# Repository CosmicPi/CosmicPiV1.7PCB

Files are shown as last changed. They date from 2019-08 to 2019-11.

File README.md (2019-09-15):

# CosmicPiV1.6
Version 1.6 of the Cosmic Pi, learning the lessons from V2 and going back to something simpler. All the components are now on a single PCB with a snap-off for the SiPM elements. We have also moved to KiCad!

The SiPM's in this design are from Ketek, and we're very happy with the performance. You can find the SiPM datasheet here: https://www.ketek.net/wp-content/uploads/2018/12/KETEK-PM3325-WB-D0-Datasheet.pdf
The SiPM's are also available to purchase retail from their shop (!) - a significant advance over our previous models:
https://www.ketek.net/store/products/pm3325-wb/

The design uses scintillators from Amcrys http://www.amcrys.com/ which are not yet available via a retail outlet, however any BC-408 equivalent scintillator that has diamond polished finish surfaces and dimensions of 200x100x10mm can be mated to the SiPMs with suitable mounting holes.

# What do the signals do?

Shapeout 1 & 2 - Shaped (i.e. amplified and stretched signal from the SiPMs - muon detection waveforms). Not used in current software.

Biasfb 1 & 2 - Feedback on the Vbias supply (i.e. to check that it's the right voltage). Not used in current software.

Inj led 1 & 2 - Light injector LEDs, allowing the operation of the SiPM to be checked (and calibrated) post-assembly. 

Accint 1, 2 - Interrupts from the accelerometer, not really used for anything yet.

Magint 3 - Interrupt from magnetometer, also not used.

Flag, boot0 - Signals to the Raspberry Pi, flag can be set by the STM32 to indicate a particular condition. Boot0 is used to set the boot mode of the STM32, for example when flashing. This doesn't function correctly in this version, it will be updated for V1.7, due to some issues with the STM32 bootloader.

Vbusm otg dm otg dp - Vbus is the USB bus voltage detection line to the STM32 (i.e. in OTG mode, sense incoming voltage), DM and DP are the differential lines for USB communication. Not functional in the current software; note that the USB doesn't power the device.

Swclk, swdio - These are the programming commands for the STM32, based on the ST-Link system. These work fine, used for programming.

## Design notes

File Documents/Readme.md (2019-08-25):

Here are some documents for the verification of the mechanical drawings. Your help is requested in checking the mechanical fit of our board with the holes we're getting machined in the box. Please take a look and share with us your comments about the mechanical design.

The board will be fixed to the chassis with 4 metal M3 thread screws with plastic washers. The front plate will be held in place by the structrure of the chassis.

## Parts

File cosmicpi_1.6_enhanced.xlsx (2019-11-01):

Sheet: Sheet1
Id | Designator | Supplier | SKY | Manufacturer | MPN (Manufacturer Part Number) | Quantity | Alternative | Comments | Package | Value | Voltage | Tolerance | Wattage
1 | D5,D6 | RS | 687-2779 | Taiwan Semi | BAS70-04 RF | 2 | BAS70-04LT1G |  | SOT-23 | BAS70-04
2 | R46,R47 | RS | 179-9597 | Panasonic | ERA3AEB512V | 2 | NTR06B5101CTR1KF |  | R_0603_1608Metric | 5100 |  | 1% | 100mW
3 | FL2, FL1 | RS | 770-7133 | Wurth | 744235220 | 2 | 123-4666 | Alternative is RS-PRO | IND_744232090 | EMI_Filter_CommonMode
4 | J14,J8,J11,J12 | RS | 701-9773 | Preci-Dip | 800-80-002-20-001101 | 4 | 830-80-002-20-001101 |  | PinHeader_1x02_P2.54mm_Horizontal | Conn_01x02_Male
5 | J9,J10,J13,J15 | RS | 766-6604 | Samtec | CES-102-01-T-S | 4 |  |  | PinHeader_1x02_P2.54mm_Vertical | Conn_01x02_Female
6 | D4,D3 | RS | 792-0787 | Nexperia | BAT46WH | 2 |  |  | D_SOD-123F | BAT46
7 | J2 | RS | 759-5299 | Molex | 73251-1150 | 1 |  |  | SMA_Molex_73251-1153_EdgeMount_Horizontal | SMA
8 | C27,C29,C34,C35,C64,C74,C14,C55,C54,C53,C50,C49,C44,C43,C66,C2,C5,C6,C7,C8,C72,C11,C12,C65,C23,C18,C70,C17,C15,C67 | RS | 669-8767 | Yageo | CC0603KRX7R9BB104 | 30 |  |  | C_0603_1608Metric | 100n | 50V
9 | C57 | RS | 915-9114 | TDK | C1608X5R1A226M080AC | 1 | GRM188R61A226ME15D |  | C_0603_1608Metric | 22u | 10V | 20%
10 | C30,C31,C41,C59,C22,C16 | RS | 616-9537 | Yageo | CC0603KRX7R9BB103 | 6 |  |  | C_0603_1608Metric | 10n | 50V
11 | C32,C33,C61,C60,C19 | Farnell | 722250 | Yageo | CC0603KRX7R8BB224 | 5 |  |  | C_0603_1608Metric | 220n | 25V
12 | C56,C13,C24 | RS | 884-7166 | Murata | GRM188B31A106ME69D | 3 |  |  | C_0603_1608Metric | 10u | 10V
13 | C46,C45 | RS | 815-1531 | Murata | GRM1885C2A300JA01D | 2 |  |  | C_0603_1608Metric | 30p | 100V
14 | C3,C4 | RS | 773-8446 | Syfer | 0603Y1000220JCT | 2 | CL10C220FB8NNND |  | C_0603_1608Metric | 22p | 16V | 5%
15 | C71,C73 | Farnell | 1828913 | Murata | GRM1885C1H102FA01D | 2 | GRM1881X1H102JA01D |  | C_0603_1608Metric | 1n | 50V | 5%
16 | C68,C69 | Farnell | 1414642 | Kemet | C0603C472K5RACTU | 2 | C0603C473K5RACAUTO |  | C_0603_1608Metric | 47n | 50V | 10%
17 | C47,C48 | Farnell | 2773209 | Kemet | C0805C104M3RACTU | 2 |  |  | C_0805_2012Metric | 100n
18 | C9,C10,C52,C51 |  |  |  |  | 4 |  | DNP | C_1206_3216Metric | n.a.
19 | C20,C75,C25,C62,C63,C58,C21,C28,C26,C40,C37,C38,C36,C39,C42 | Farnell | 9227873 | Kemet | C1206C105Z3VACTU | 15 |  |  | C_1206_3216Metric | 1u | 25V | -20%->+80%
20 | C76 | RS | 172-1612 | Taiyo Yuden | JMK316BBJ107MLHT | 1 |  |  | C_1206_3216Metric | 100u | 6.3V | 20%
21 | C1 | RS | 766-1037 | Samsung | CL21B475KOFNNNG | 1 | C0805C475K3PACTU |  | C_0805_2012Metric | 4.7u | 16V | 10%
22 | J1 | RS | 122-4879 | Wurth | 694106301002 | 1 |  |  | BarrelJack_Horizontal | Barrel_Jack_Switch
23 | J6 | Farnell | 2847171 | Multicomp | 2211SM-06G-B1-TB | 1 | TSM-106-01-T-SV |  | PinSocket_1x06_P2.54mm_Vertical_SMD_Pin1Left | SWD
24 | J7 | Farnell | 2847928 | Multicomp | 2214SM-20G-75-PCR | 1 | CLH-110-F-D-BE |  | PinSocket_2x20_P2.54mm_Vertical_SMD | Raspberry_Pi_2_3
25 | J3 | Farnell | 2293836 | Molex | 105017-0001 | 1 |  |  | USB_Micro-B_Molex-105017-0001 | USB_B_Micro
26 | J4, J5 |  |  |  | PM3325-WB | 2 |  | Customer Supplied | Ketek_PM3325-WB | SiPM1
27 | U3 | RS | 908-4108 | Quectel | L76-M33 | 1 | L70B-M39 |  | LM76-M33 | L76-M33
28 | Y1 | RS | 178-2555 | CTS | ATS08ASM-1E | 1 |  |  | Crystal:Crystal_SMD_HC49-SD | 8 MHz
29 | L3 | RS | 496-0978 | EPCOS | B82496C3470J000 | 1 |  |  | L_0603_1608Metric | 47nH
30 | L1 | RS | 604-1489 | TDK | MLZ1608A2R2MT | 1 |  | BRL1608T2R2M | L_0603_1608Metric | 2.2uH
31 | L4,L2 | Farnell | 1612672 | Bourns | CM453232-151KL | 2 |  |  | L_1812_4532Metric | 150uH
32 | D2,D8,D7,D1 | Farnell | 2426212 | Kingbright | KPH-1608QBC-D | 4 | KPG-1608QBC-D |  | LED_0603_1608Metric | LED
33 | U8 | Farnell | 2473659 | Silicon Labs | Si7006-A20-IM | 1 |  |  | DFN-6-1EP_3x3mm_P1mm_EP1.5x2.4mm | SI7006-A20
34 | U17,U18 | Digikey | MAX1932ETC+TCT-ND | Maxim | MAX1932ETC+ | 2 |  |  | 21-0136I_T1233-3 | MAX1932
35 | U7 | Farnell | 2532383RL | ST | LSM9DS1TR | 1 |  |  | LGA-24L_3x3.5mm_P0.43mm | LSM9DS1
36 | U5 | Farnell | 2474251 | ST | LPS25HBTR | 1 |  |  | ST_HLGA-10_2.5x2.5mm_P0.6mm_LayoutBorder3x2y | LPS25HB
37 | U2 | RS | 110-6614 | ST | STM32F401RET6 | 1 |  |  | LQFP-64_10x10mm_P0.5mm | STM32F401RETx
38 | U1 | Digikey | MCP47CMB12-E/UN-ND | Microchip | MCP47CMB12-E/UN | 1 | MCP47CMB22-E/UN |  | MSOP-10_3x3mm_P0.5mm | MCP47CMB22
39 | U4 | RS | 798-8985 | DiodesZetex | 74HC00S14-13 | 1 | 74HC00D |  | SOIC-14_3.9x8.7mm_P1.27mm | 74HC00
40 | U6,U11,U12 | RS | 121-8948 | TI | TLC555ID | 3 |  |  | SOIC-8_3.9x4.9mm_P1.27mm | LM555
41 | U19,U14,U15 | RS | 912-7432 | Analog Devices | AD8039ARZ | 3 |  |  | SOIC-8_3.9x4.9mm_P1.27mm | AD8039
42 | U9 | Farnell | 2515037 | Maxim | MAX991ESA+ | 1 |  |  | SOIC-8_3.9x4.9mm_P1.27mm | MAX991
43 | U10 | RS | 825-6949 | TI | TPS62163DSGT | 1 | TPS62163DSGR |  | WSON-8-1EP_2x2mm_P0.5mm_EP0.9x1.6mm_ThermalVias | TPS62163DSG
44 | Q2,Q1 | RS | 671-0321 | On Semiconductor | BSS123 | 2 | BSS123W |  | SOT-23 | BSS123
45 | U13,U16 | Farnell | 1469134 | TI | LP2985AIM5-3.3/NOPB | 2 | LP2985IM5-3.3/NOPB |  | SOT-23-5 | LP2985-3.3
46 | R33,R32 | Farnell | 2331995 | TE | CRG0603F330R | 2 |  |  | R_0603_1608Metric | 330R |  | 1% | 100mW
47 | R57,R49,R23,R59,R21,R15,R14,R61,R9,R5,R36,R35,R34,R22,R37,R29,R28,R27,R26,R25,R24 | Farnell | 1469748RL | Vishay | CRCW060310K0FKEA | 21 |  |  | R_0603_1608Metric | 10k |  | 1% | 100mW
48 | R48 | Farnell | 1670194 | Panasonic | ERA3AEB203V | 1 |  |  | R_0603_1608Metric | 20k |  | 1% | 100mW
49 | R50,R51,R45,R44,R43,R42 | RS | 213-2266 | TE | CRG0603F1K0 | 6 |  |  | R_0603_1608Metric | 1k |  | 1% | 100mW
50 | R52,R53 | RS | 179-9591 | Panasonic | ERA3AEB303V | 2 |  |  | R_0603_1608Metric | 30k |  | 1% | 100mW
51 | R54,R55,R64,R66,R67,R69 | RS | 176-3495 | Panasonic | ERJ3EKF1000V | 6 |  |  | R_0603_1608Metric | 100 |  | 1% | 100mW
52 | R56,R58,R60,R20 | RS | 678-9967 | Vishay | CRCW0603200KFKEA | 4 |  |  | R_0603_1608Metric | 200k |  | 1% | 100mW
53 | R63,R7,R62,R6 | RS | 679-0172 | Vishay | CRCW0603300RFKEA | 4 |  |  | R_0603_1608Metric | 300 |  | 1% | 100mW
54 | R65,R68 | Farnell | 2138570 | Vishay | CRCW0603510KFKEA | 2 | CRCW0603499KFKEA |  | R_0603_1608Metric | 510k |  | 1% | 100mW
55 | R19,R18 | Farnell | 1469785 | Vishay | CRCW060324K9FKEA | 2 |  |  | R_0603_1608Metric | 24.9k |  | 1% | 100mW
56 | R17,R16 | RS | 106-2936 | Panasonic | ERJP03F8060V | 2 |  |  | R_0603_1608Metric | 806 |  | 1% | 100mW
57 | R41,R2,R31,R40,R39,R38,R30 | RS | 678-9673 | Vishay | CRCW0603100KFKEA | 7 | CRCW0603100KJNEAIF |  | R_0603_1608Metric | 100k |  | 1% | 100mW
58 | R13 | Farnell | 1469751 | Vishay | CRCW060310R0FKEA | 1 | CR0603-FX-10R0ELF |  | R_0603_1608Metric | 10 |  | 1% | 100mW
59 | R11,R12 | Farnell | 1469758 | Vishay | CRCW060315K0FKEA | 2 | CRGP0603F15K |  | R_0603_1608Metric | 15k |  | 1% | 100mW
60 | R8 | Farnell | 2616741 | Vishay | CRCW06030000Z0EB | 1 |  |  | R_0603_1608Metric | 0R
61 | R70,R10, R3,R4,R1 | Farnell | 2380162 | Panasonic | ERJ3RED20R0V | 5 | CRCW060320R0FKEA |  | R_0603_1608Metric | 20 |  | 1% | 100mW

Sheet: cosmicpi_1.6
Id;"Designator";"Package";"Quantity";"Designation";"Supplier and ref";
1;"D5 | D6";"SOT-23";2;"BAS70-04";;;
2;"R46 | R47";"R_0603_1608Metric";2;"5100";;;
3;"H5 | H6 | H2 | H4 | H3 | H1";"MountingHole_3.7mm";6;"MountingHole_3.7mm";;;
4;"FL2";"IND_744232090";1;"EMI_Filter_CommonMode";;;
5;"FL1";"IND_744232090";1;"CM choke";;;
6;"J14 | J8 | J11 | J12";"PinHeader_1x02_P2.54mm_Horizontal";4;"Conn_01x02_Male";;;
7;"J9 | J10 | J13 | J15";"PinHeader_1x02_P2.54mm_Vertical";4;"Conn_01x02_Female";;;
8;"D4 | D3";"D_SOD-123F";2;"BAT46";;;
9;"J2";"SMA_Molex_73251-1153_EdgeMount_Horizontal";1;"SMA";;;
10;"C27 | C29 | C34 | C35 | C64 | C74 | C14 | C55 | C54 | C53 | C50 | C49 | C44 | C43 | C66 | C2 | C5 | C6 | C7 | C8 | C72 | C11 | C12 | C65 | C23 | C18 | C70 | C17 | C15 | C67";"C_0603_1608Metric";30;"100n";;;
11;"C57";"C_0603_1608Metric";1;"22u";;;
12;"C30 | C31 | C41 | C59 | C22 | C16";"C_0603_1608Metric";6;"10n";;;
13;"C32 | C33 | C61 | C60 | C19";"C_0603_1608Metric";5;"220n";;;
14;"C56 | C13 | C24";"C_0603_1608Metric";3;"10u";;;
15;"C46 | C45";"C_0603_1608Metric";2;"30p";;;
16;"C3 | C4";"C_0603_1608Metric";2;"22p";;;
17;"C71 | C73";"C_0603_1608Metric";2;"1n";;;
18;"C68 | C69";"C_0603_1608Metric";2;"47n";;;
19;"C47 | C48";"C_0805_2012Metric";2;"100n";;;
20;"C9 | C10 | C52 | C51";"C_1206_3216Metric";4;"n.a.";;;
21;"C20 | C75 | C25 | C62 | C63 | C58 | C21 | C28 | C26 | C40 | C37 | C38 | C36 | C39 | C42";"C_1206_3216Metric";15;"1u";;;
22;"C76";"C_1206_3216Metric";1;"100u";;;
23;"C1";"CP_EIA-6032-15_Kemet-U";1;"2.2u";;;
24;"J1";"BarrelJack_Horizontal";1;"Barrel_Jack_Switch";;;
25;"J6";"PinSocket_1x06_P2.54mm_Vertical_SMD_Pin1Left";1;"SWD";;;
26;"J7";"PinSocket_2x20_P2.54mm_Vertical_SMD";1;"Raspberry_Pi_2_3";;;
27;"J3";"USB_Micro-B_Molex-105017-0001";1;"USB_B_Micro";;;
28;"J4";"Ketek_PM3325-WB";1;"SiPM1";;;
29;"J5";"Ketek_PM3325-WB";1;"SiPM2";;;
30;"U3";"LM76-M33";1;"L76-M33";;;
31;"Y1";"Crystal_SMD_G8-2Pin_3.2x1.5mm";1;"8 MHz";;;
32;"L3";"L_0603_1608Metric";1;"47nH";;;
33;"L1";"L_0603_1608Metric";1;"2.2u";;;
34;"L4 | L2";"L_1812_4532Metric";2;"150uH";;;
35;"D2 | D8 | D7 | D1";"LED_0603_1608Metric";4;"LED";;;
36;"U8";"DFN-6-1EP_3x3mm_P1mm_EP1.5x2.4mm";1;"SI7006-A20";;;
37;"U17 | U18";"QFN-16-1EP_4x4mm_P0.65mm_EP2.5x2.5mm";2;"MAX1932";;;
38;"U7";"LGA-24L_3x3.5mm_P0.43mm";1;"LSM9DS1";;;
39;"U5";"ST_HLGA-10_2.5x2.5mm_P0.6mm_LayoutBorder3x2y";1;"LPS25HB";;;
40;"U2";"LQFP-64_10x10mm_P0.5mm";1;"STM32F401RETx";;;
41;"U1";"MSOP-10_3x3mm_P0.5mm";1;"MCP47CMB22";;;
42;"U4";"SOIC-14_3.9x8.7mm_P1.27mm";1;"74HC00";;;
43;"U6 | U11 | U12";"SOIC-8_3.9x4.9mm_P1.27mm";3;"LM555";;;
44;"U19 | U14 | U15";"SOIC-8_3.9x4.9mm_P1.27mm";3;"AD8039";;;
45;"U9";"SOIC-8_3.9x4.9mm_P1.27mm";1;"MAX991";;;
46;"U10";"WSON-8-1EP_2x2mm_P0.5mm_EP0.9x1.6mm_ThermalVias";1;"TPS62163DSG";;;
47;"Q2 | Q1";"SOT-23";2;"BSS123";;;
48;"U13 | U16";"SOT-23-5";2;"LP2985-3.3";;;
49;"R33 | R32";"R_0603_1608Metric";2;"330R";;;
50;"R57 | R49 | R23 | R59 | R21 | R15 | R14 | R61 | R9 | R5 | R36 | R35 | R34 | R22 | R37 | R29 | R28 | R27 | R26 | R25 | R24";"R_0603_1608Metric";21;"10k";;;
51;"R48";"R_0603_1608Metric";1;"20k";;;
52;"R50 | R51 | R44 | R43 | R42";"R_0603_1608Metric";5;"1k";;;
53;"R52 | R53";"R_0603_1608Metric";2;"30k";;;
54;"R54 | R55 | R64 | R66 | R67 | R69";"R_0603_1608Metric";6;"100";;;
55;"R56 | R58 | R60 | R20";"R_0603_1608Metric";4;"200k";;;
56;"R45";"R_0603_1608Metric";1;"1l";;;
57;"R63 | R7 | R62 | R6";"R_0603_1608Metric";4;"300";;;
58;"R65 | R68";"R_0603_1608Metric";2;"500k";;;
59;"R19 | R18";"R_0603_1608Metric";2;"24.9k";;;
60;"R17 | R16";"R_0603_1608Metric";2;"806";;;
61;"R41 | R2 | R31 | R40 | R39 | R38 | R30";"R_0603_1608Metric";7;"100k";;;
62;"R13";"R_0603_1608Metric";1;"10";;;
63;"R11 | R12";"R_0603_1608Metric";2;"15k";;;
64;"R8";"R_0603_1608Metric";1;"0R";;;
65;"R3 | R4 | R1";"R_0603_1608Metric";3;"20";;;

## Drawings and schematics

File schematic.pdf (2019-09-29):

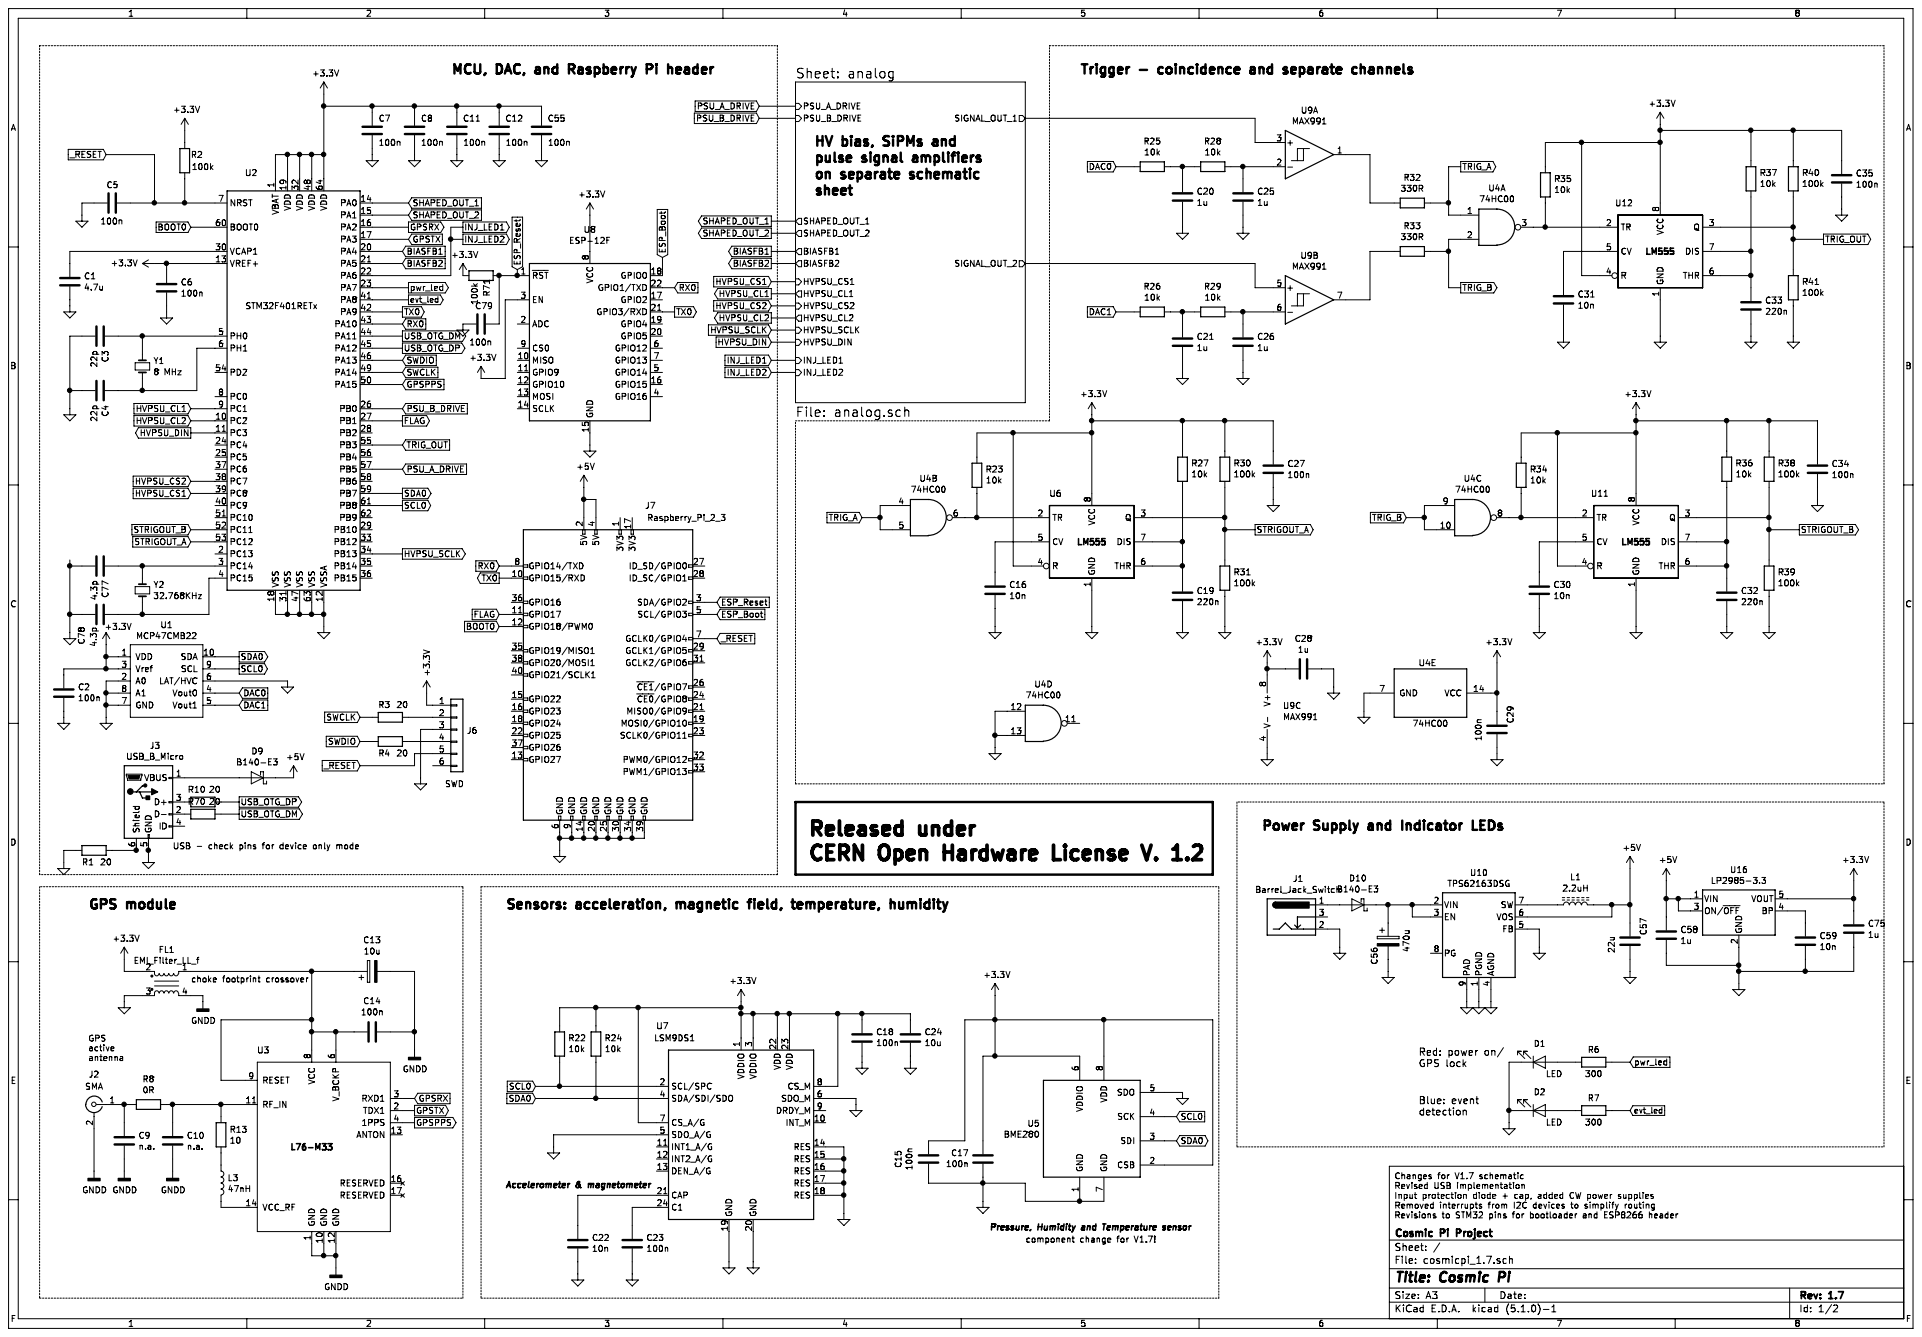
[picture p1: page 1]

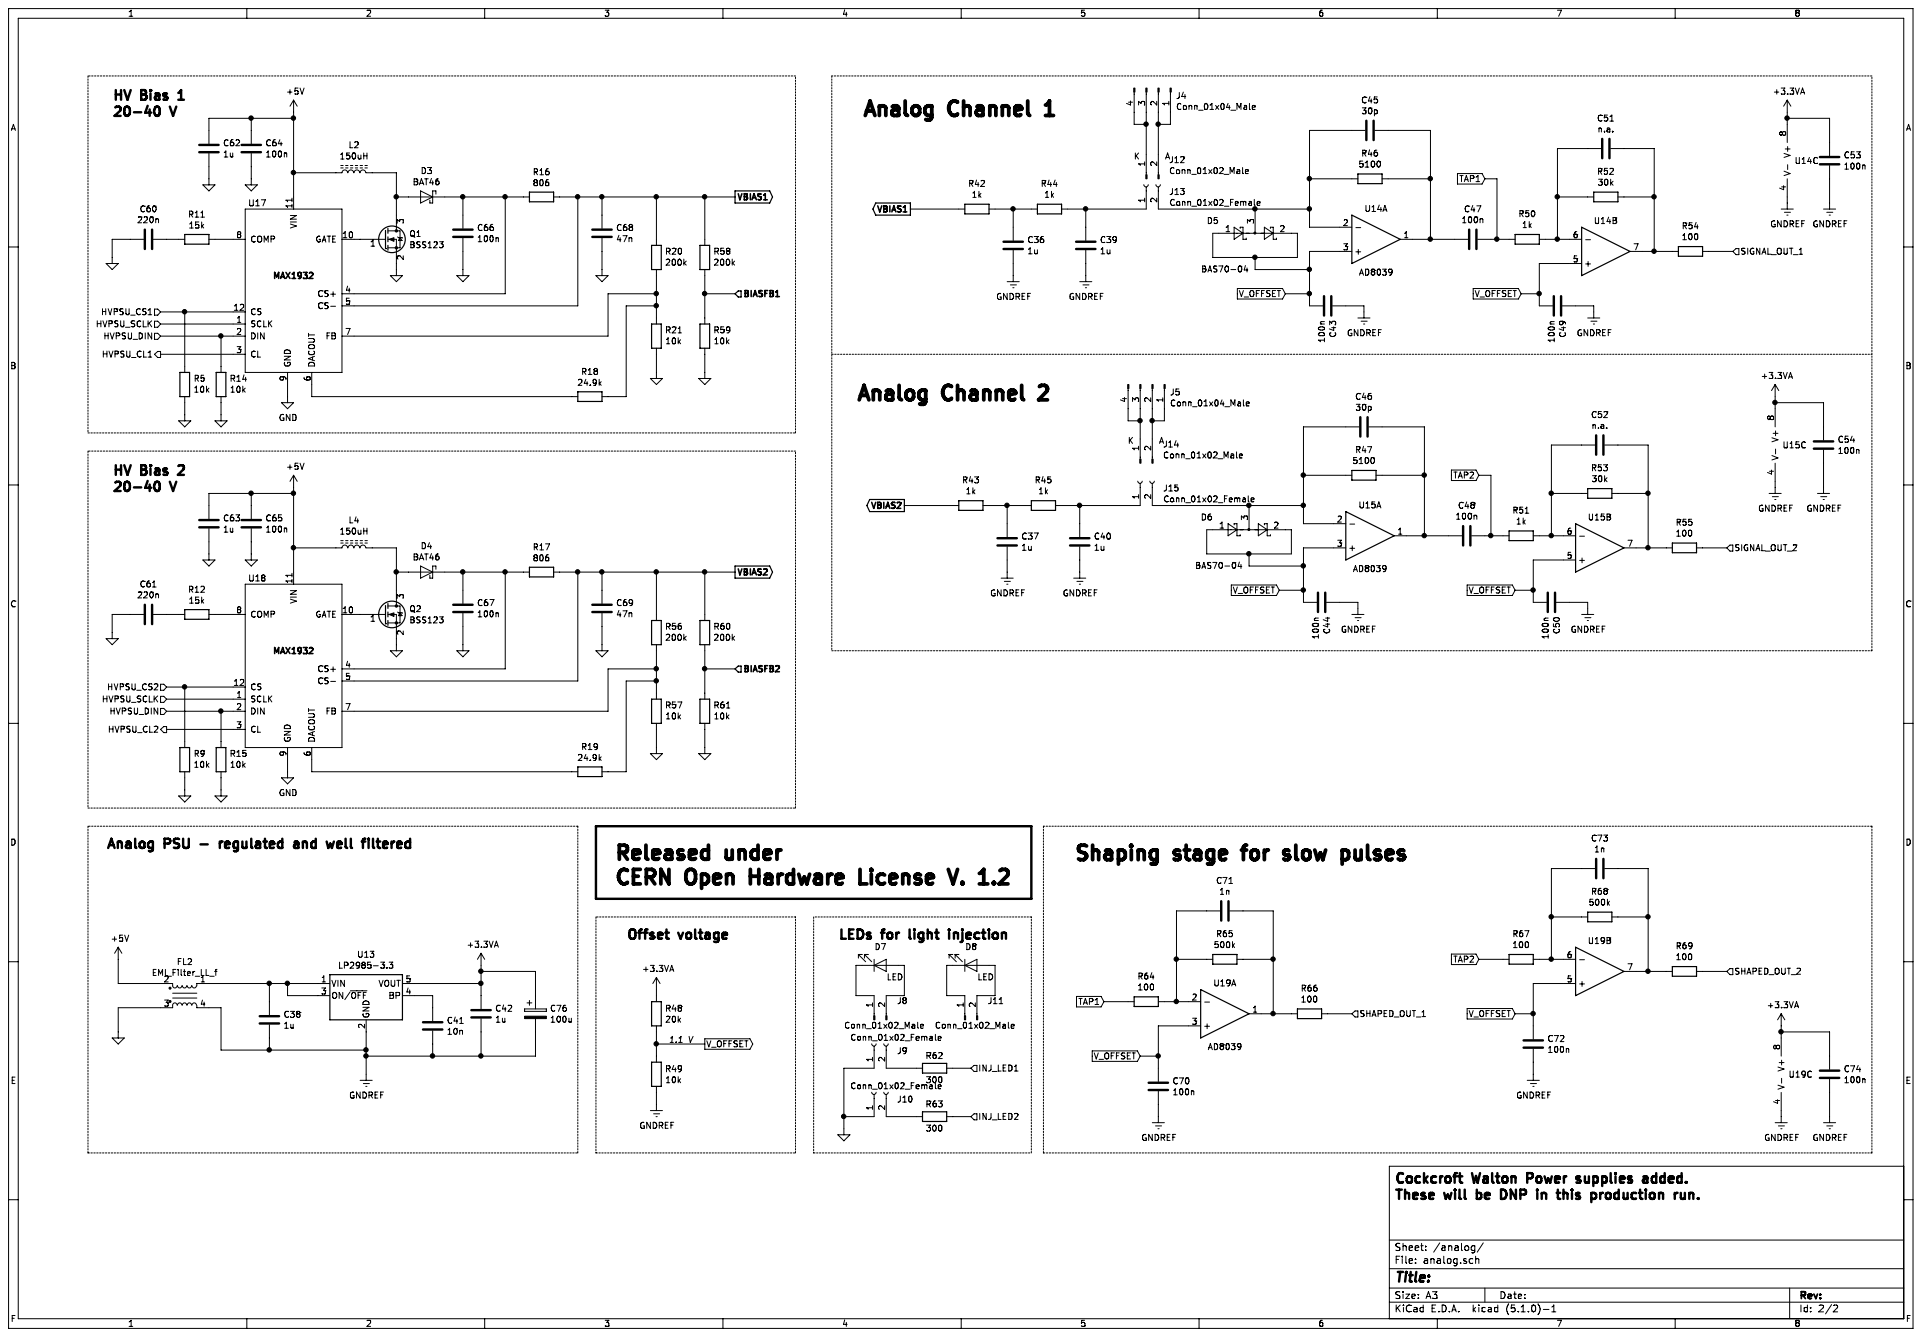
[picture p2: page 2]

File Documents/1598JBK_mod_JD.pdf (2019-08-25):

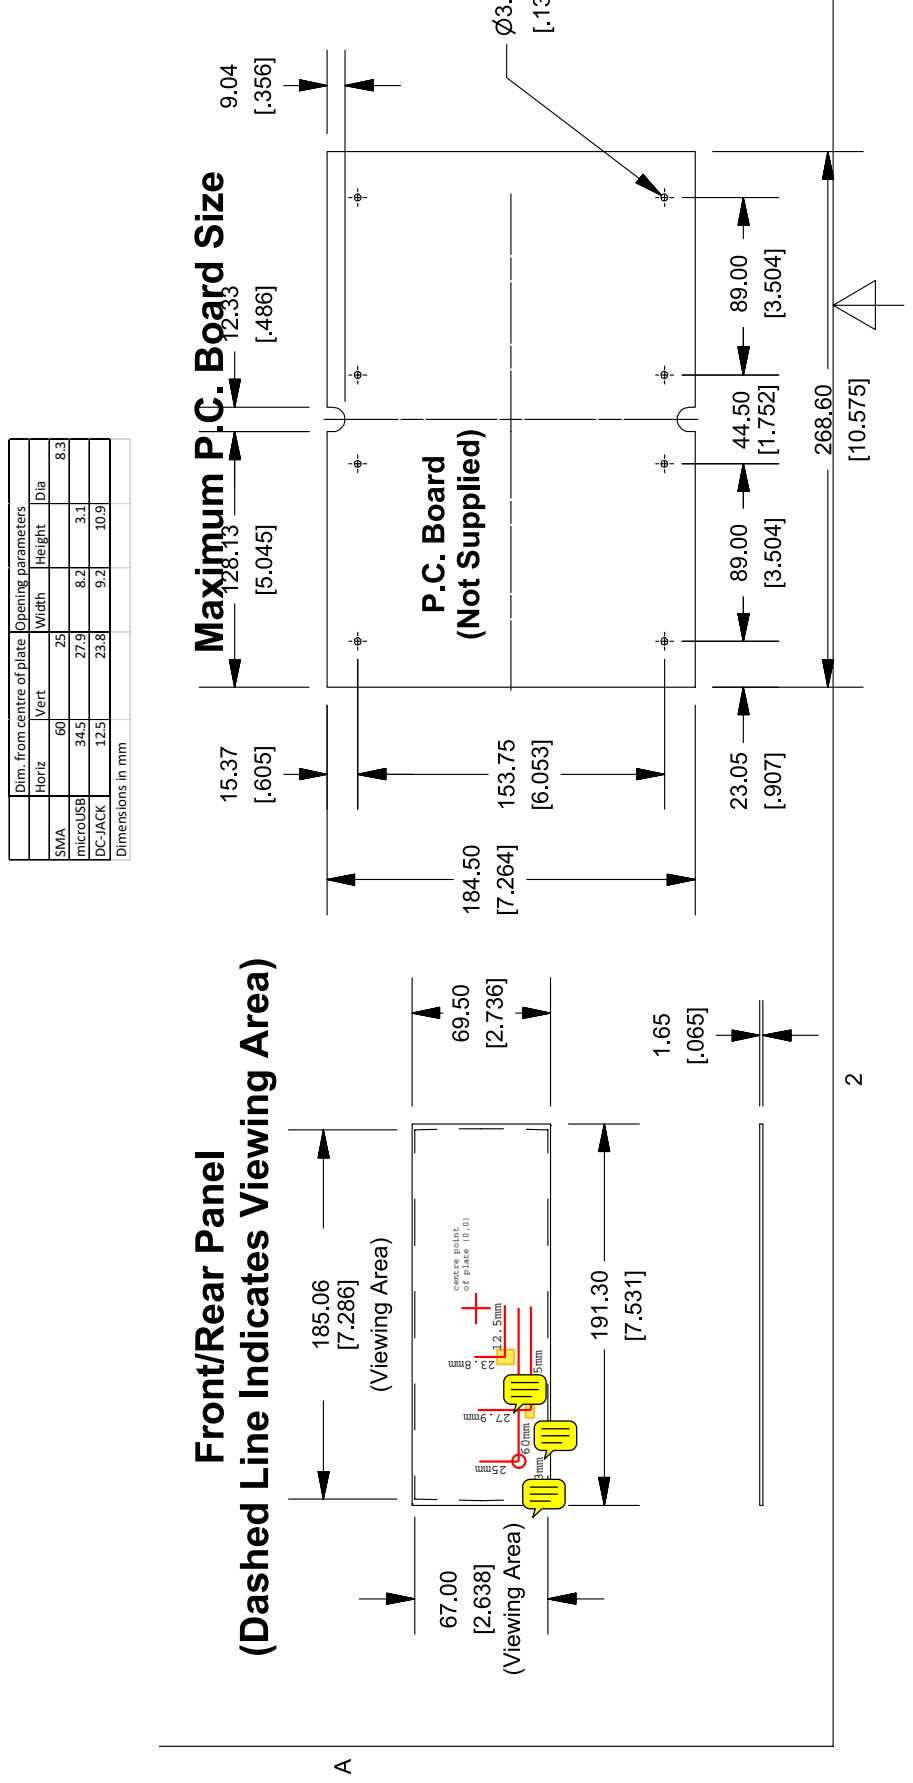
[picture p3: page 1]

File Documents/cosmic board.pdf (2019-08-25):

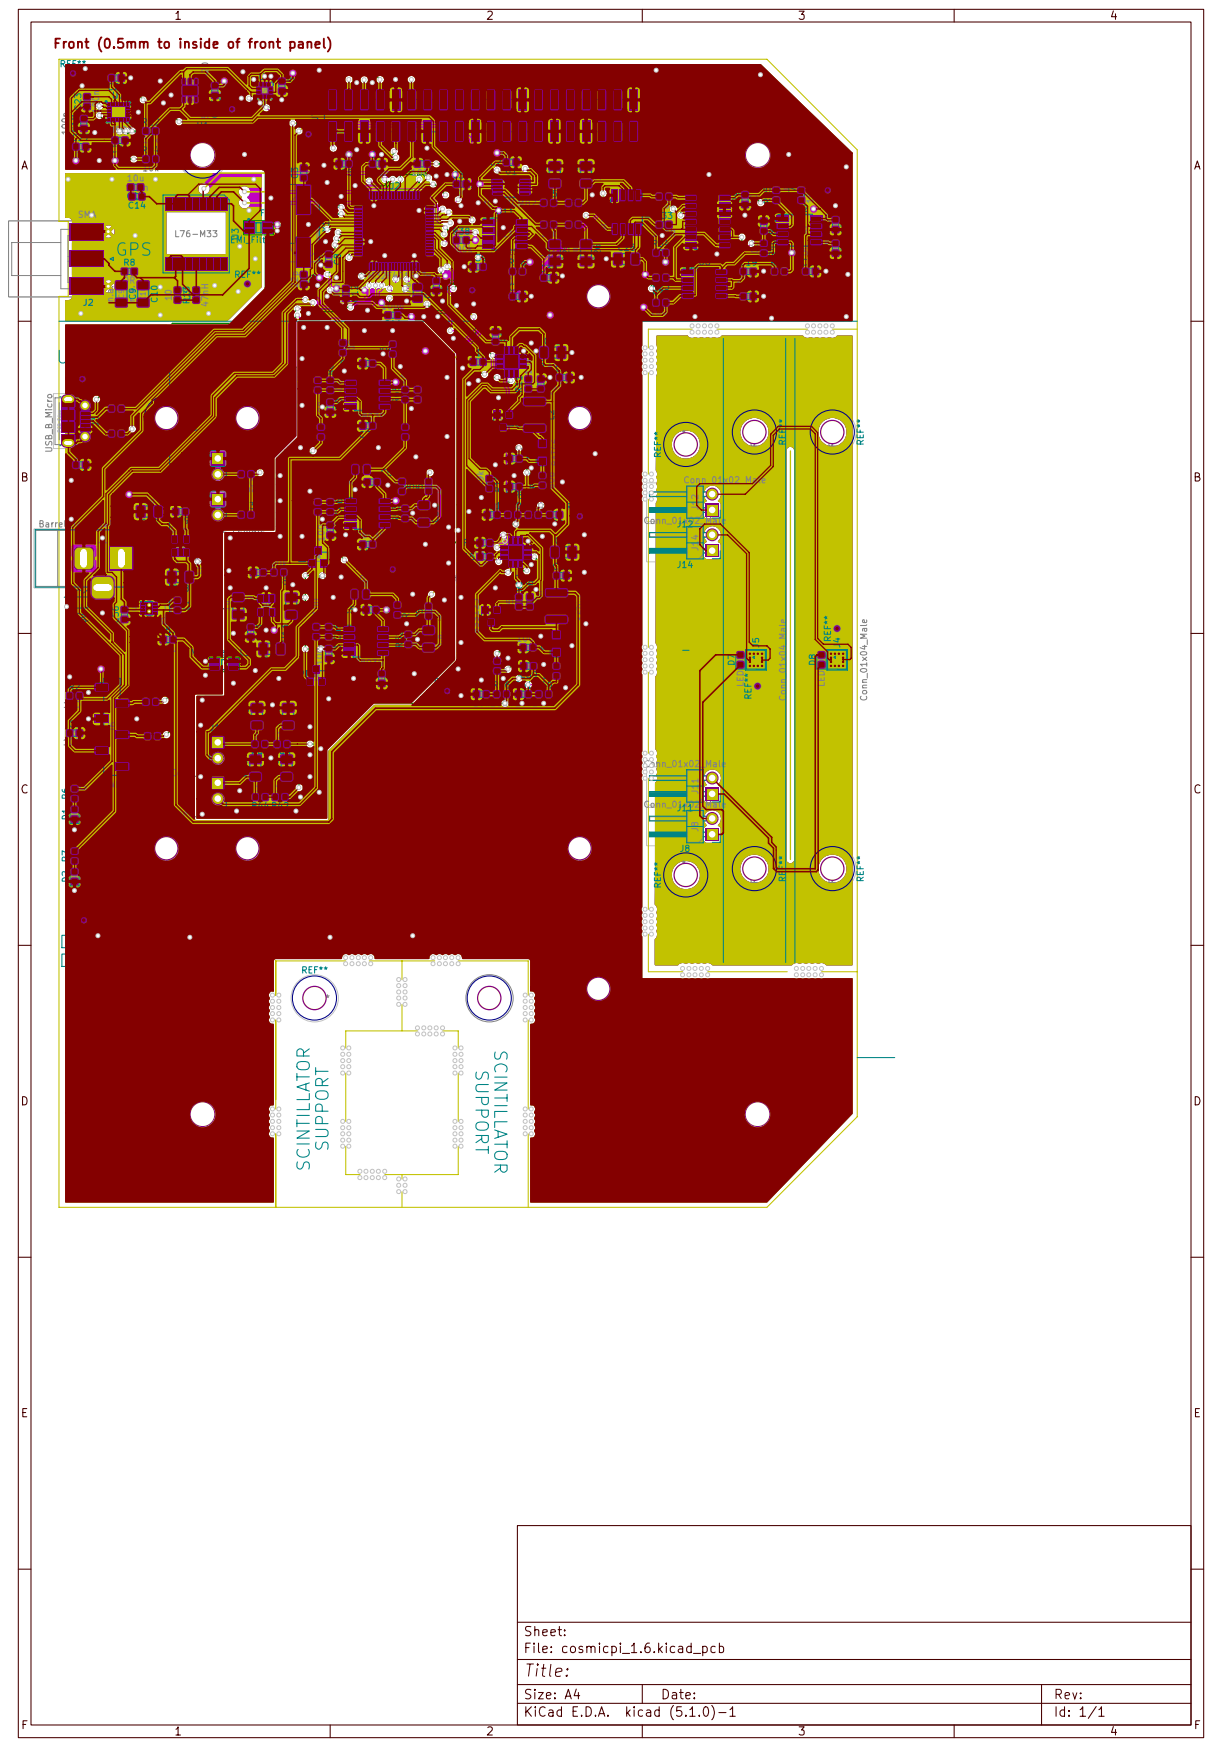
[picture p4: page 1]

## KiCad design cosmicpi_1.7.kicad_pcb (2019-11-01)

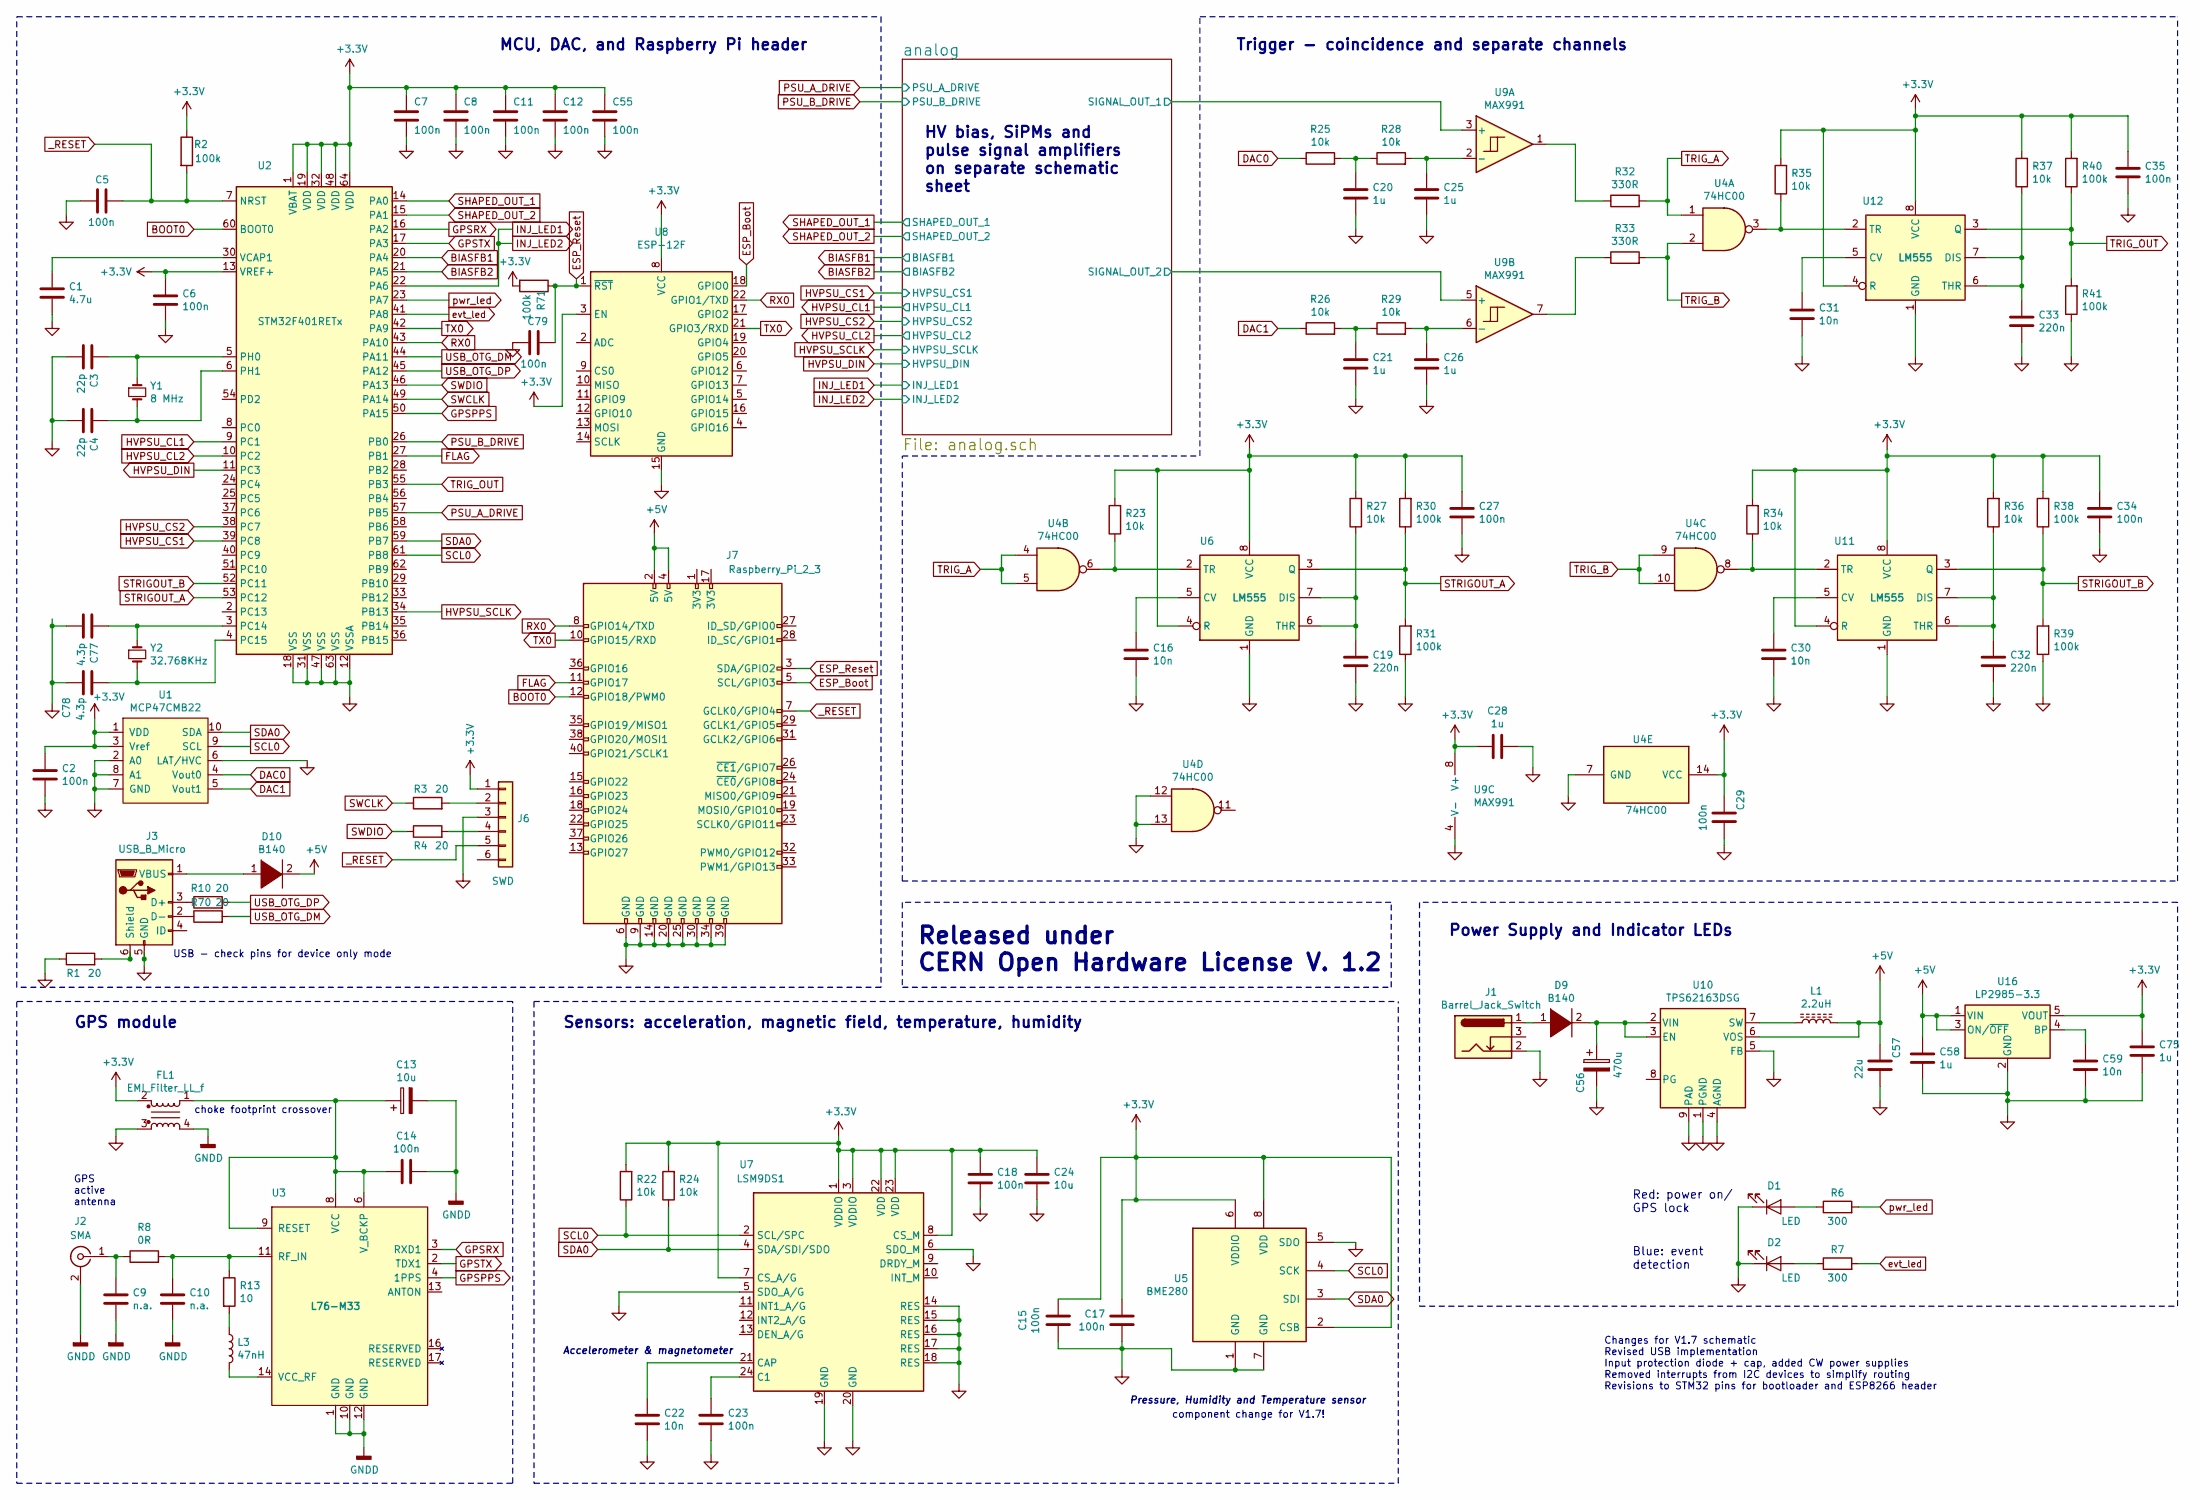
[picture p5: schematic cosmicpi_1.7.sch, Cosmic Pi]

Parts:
C1: 4.7u; C_0805_2012Metric
C2, C5, C6, C7, C8, C11, C12, C14, C15, C17, C18, C23, C27, C29, C34, C35, C55, C79: 100n; C_0603_1608Metric
C3, C4: 22p; C_0603_1608Metric
C9, C10: n.a.; C_1206_3216Metric
C13, C24: 10u; C_0603_1608Metric
C16, C22, C30, C31, C59: 10n; C_0603_1608Metric
C19, C32, C33: 220n; C_0603_1608Metric
C20, C21, C25, C26, C28, C58, C75: 1u; C_1206_3216Metric
C56: 470u; C_Elec_10x10.2
C57: 22u; C_0603_1608Metric
C77, C78: 4.3p; C_0603_1608Metric
D1, D2: LED; LED_0603_1608Metric
D9, D10: B140; D_SMA
FL1: EMI_Filter_LL_f; IND_744232090
J1: Barrel_Jack_Switch; BarrelJack_Horizontal
J2: SMA; SMA_Molex_73251-1153_EdgeMount_Horizontal
J3: USB_B_Micro; USB_Micro-B_Molex-105017-0001
J6: SWD; PinSocket_1x06_P2.54mm_Vertical_SMD_Pin1Left
J7: Raspberry_Pi_2_3; PinSocket_2x20_P2.54mm_Vertical_SMD
L1: 2.2uH; L_0603_1608Metric
L3: 47nH; L_0603_1608Metric
R1, R3, R4, R10, R70: 20; R_0603_1608Metric
R2, R30, R31, R38, R39, R40, R41, R71: 100k; R_0603_1608Metric
R6, R7: 300; R_0603_1608Metric
R8: 0R; R_0603_1608Metric
R13: 10; R_0603_1608Metric
R22, R23, R24, R25, R26, R27, R28, R29, R34, R35, R36, R37: 10k; R_0603_1608Metric
R32, R33: 330R; R_0603_1608Metric
U1: MCP47CMB22; MSOP-10_3x3mm_P0.5mm
U2: STM32F401RETx; LQFP-64_10x10mm_P0.5mm
U3: L76-M33; LM76-M33
U4: 74HC00; SOIC-14_3.9x8.7mm_P1.27mm
U5: BME280; Bosch_LGA-8_2.5x2.5mm_P0.65mm_ClockwisePinNumbering
U6, U11, U12: LM555; SOIC-8_3.9x4.9mm_P1.27mm
U7: LSM9DS1; LGA-24L_3x3.5mm_P0.43mm
U8: ESP-12F; ESP-12E
U9: MAX991; SOIC-8_3.9x4.9mm_P1.27mm
U10: TPS62163DSG; WSON-8-1EP_2x2mm_P0.5mm_EP0.9x1.6mm_ThermalVias
U16: LP2985-3.3; SOT-23-5
Y1: 8 MHz; Crystal_SMD_HC49-SD
Y2: 32.768KHz; Crystal_SMD_HC49-SD

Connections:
+3V3: C2.2, C6.1, C7.1, C8.1, C11.1, C12.1, C15.2, C17.2, C18.2, C24.2, C27.1, C28.2, C29.2, C34.1, C35.1, C55.1, C75.1, FL1.2, J6.1, R2.1, R22.2, R23.2, R24.2, R27.2, R30.2, R34.2, R35.2, R36.2, R37.2, R38.2, R40.2, R71.2, U1.1 (VDD), U1.3 (Vref), U2.1 (VBAT), U2.13 (VREF+), U2.19 (VDD), U2.32 (VDD), U2.48 (VDD), U2.64 (VDD), U4.14 (VCC), U5.2 (CSB), U5.6 (VDDIO), U5.8 (VDD), U6.4 (R), U6.8 (VCC), U7.1 (VDDIO), U7.3 (VDDIO), U7.7 (CS_A/G), U7.8 (CS_M), U7.22 (VDD), U7.23 (VDD), U8.3 (EN), U8.8 (VCC), U9.8 (V+), U11.4 (R), U11.8 (VCC), U12.4 (R), U12.8 (VCC), U16.5 (VOUT)
/analog/SIGNAL_OUT_1: U9.3 (+); also elsewhere on the board
/analog/SIGNAL_OUT_2: U9.5 (+); also elsewhere on the board
BIASFB1: U2.20 (PA4); also elsewhere on the board
BIASFB2: U2.21 (PA5); also elsewhere on the board
BOOT0: J7.12 (GPIO18/PWM0), U2.60 (BOOT0)
DAC0: R25.1, U1.4 (Vout0)
DAC1: R26.1, U1.5 (Vout1)
ESP_Boot: J7.5 (SCL/GPIO3), U8.18 (GPIO0)
ESP_Reset: C79.1, J7.3 (SDA/GPIO2), R71.1, U8.1 (~RST)
FLAG: J7.11 (GPIO17), U2.27 (PB1)
GND: C1.2, C2.1, C3.2, C4.2, C5.2, C6.2, C7.2, C8.2, C11.2, C12.2, C15.1, C16.2, C17.1, C18.1, C19.2, C20.2, C21.2, C22.1, C23.1, C24.1, C25.2, C26.2, C27.2, C28.1, C29.1, C30.2, C31.2, C32.2, C33.2, C34.2, C35.2, C55.2, C56.2, C57.1, C58.2, C59.2, C75.2, C77.2, C78.2, C79.2, D1.1 (K), D2.1 (K), FL1.3, J1.2, J3.5 (GND), J6.3, J7.6 (GND), J7.9 (GND), J7.14 (GND), J7.20 (GND), J7.25 (GND), J7.30 (GND), J7.34 (GND), J7.39 (GND), R1.1, R31.1, R39.1, R41.1, U1.2 (A0), U1.6 (LAT/HVC), U1.7 (GND), U1.8 (A1), U2.12 (VSSA), U2.18 (VSS), U2.31 (VSS), U2.47 (VSS), U2.63 (VSS), U4.7 (GND), U4.12, U4.13, U5.1 (GND), U5.5 (SDO), U5.7 (GND), U6.1 (GND), U7.5 (SDO_A/G), U7.6 (SDO_M), U7.14 (RES), U7.15 (RES), U7.16 (RES), U7.17 (RES), U7.18 (RES), U7.19 (GND), U7.20 (GND), U8.15 (GND), U9.4 (V-), U10.1 (PGND), U10.4 (AGND), U10.5 (FB), U10.9 (PAD), U11.1 (GND), U12.1 (GND), U16.2 (GND); also elsewhere on the board
GNDD: C9.2, C10.2, C13.2, C14.2, FL1.4, J2.2 (Ext), U3.1 (GND), U3.10 (GND), U3.12 (GND)
GPSPPS: U2.50 (PA15), U3.4 (1PPS)
GPSRX: U2.16 (PA2), U3.3 (RXD1)
GPSTX: U2.17 (PA3), U3.2 (TDX1)
HVPSU_CL1: U2.9 (PC1); also elsewhere on the board
HVPSU_CL2: U2.10 (PC2); also elsewhere on the board
HVPSU_CS1: U2.39 (PC8); also elsewhere on the board
HVPSU_CS2: U2.38 (PC7); also elsewhere on the board
HVPSU_DIN: U2.11 (PC3); also elsewhere on the board
HVPSU_SCLK: U2.34 (PB13); also elsewhere on the board
INJ_LED1: U2.22 (PA6); also elsewhere on the board
unnamed: C1.1, U2.30 (VCAP1)
unnamed: C3.1, U2.5 (PH0), Y1.1
unnamed: C4.1, U2.6 (PH1), Y1.2
unnamed: C9.1, J2.1 (In), R8.1
unnamed: C10.1, R8.2, R13.1, U3.11 (RF_IN)
unnamed: C13.1, C14.1, FL1.1, U3.6 (V_BCKP), U3.8 (VCC), U3.9 (RESET)
unnamed: C16.1, U6.5 (CV)
unnamed: C19.1, R27.1, U6.6 (THR), U6.7 (DIS)
unnamed: C20.1, R25.2, R28.1
unnamed: C21.1, R26.2, R29.1
unnamed: C22.2, U7.21 (CAP)
unnamed: C23.2, U7.24 (C1)
unnamed: C25.1, R28.2, U9.2 (-)
unnamed: C26.1, R29.2, U9.6 (-)
unnamed: C30.1, U11.5 (CV)
unnamed: C31.1, U12.5 (CV)
unnamed: C32.1, R36.1, U11.6 (THR), U11.7 (DIS)
unnamed: C33.1, R37.1, U12.6 (THR), U12.7 (DIS)
unnamed: C59.1, U16.4 (BP)
unnamed: C77.1, U2.3 (PC14), Y2.1
unnamed: C78.1, U2.4 (PC15), Y2.2
unnamed: D1.2 (A), R6.1
unnamed: D2.2 (A), R7.1
unnamed: J3.2 (D-), R70.1
unnamed: J3.3 (D+), R10.1
unnamed: J3.6 (Shield), R1.2
unnamed: J6.2, R3.2
unnamed: J6.4, R4.2
unnamed: L1.1, U10.7 (SW)
unnamed: L3.1, R13.2
unnamed: L3.2, U3.14 (VCC_RF)
unnamed: R23.1, U4.6, U6.2 (TR)
unnamed: R32.1, U9.1
unnamed: R33.1, U9.7
unnamed: R34.1, U4.8, U11.2 (TR)
unnamed: R35.1, U4.3, U12.2 (TR)
PSU_A_DRIVE: U2.57 (PB5)
PSU_B_DRIVE: U2.26 (PB0)
RX0: J7.8 (GPIO14/TXD), U2.43 (PA10), U8.22 (GPIO1/TXD)
SCL0: R22.1, U1.9 (SCL), U2.61 (PB8), U5.4 (SCK), U7.2 (SCL/SPC)
SDA0: R24.1, U1.10 (SDA), U2.59 (PB7), U5.3 (SDI), U7.4 (SDA/SDI/SDO)
SHAPED_OUT_1: U2.14 (PA0); also elsewhere on the board
SHAPED_OUT_2: U2.15 (PA1); also elsewhere on the board
STRIGOUT_A: R30.1, R31.2, U2.53 (PC12), U6.3 (Q)
STRIGOUT_B: R38.1, R39.2, U2.52 (PC11), U11.3 (Q)
SWCLK: R3.1, U2.49 (PA14)
SWDIO: R4.1, U2.46 (PA13)
TRIG_A: R32.2, U4.1, U4.4, U4.5
TRIG_B: R33.2, U4.2, U4.9, U4.10
TRIG_OUT: R40.1, R41.2, U2.55 (PB3), U12.3 (Q)
TX0: J7.10 (GPIO15/RXD), U2.42 (PA9), U8.21 (GPIO3/RXD)
USB_OTG_DM: R70.2, U2.44 (PA11)
USB_OTG_DP: R10.2, U2.45 (PA12)
_RESET: C5.1, J6.5, J7.7 (GCLK0/GPIO4), R2.2, U2.7 (NRST)
evt_led: R7.2, U2.41 (PA8)
pwr_led: R6.2, U2.23 (PA7)

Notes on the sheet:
Trigger - coincidence and separate channels
GPS module
GPS active antenna
Sensors: acceleration, magnetic field, temperature, humidity
Released under CERN Open Hardware License V. 1.2
Power Supply and Indicator LEDs
Pressure, Humidity and Temperature sensor
Accelerometer & magnetometer
HV bias, SiPMs and pulse signal amplifiers on separate schematic sheet
Red: power on/ GPS lock
Blue: event detection
MCU, DAC, and Raspberry Pi header
choke footprint crossover
USB - check pins for device only mode
component change for V1.7!
Changes for V1.7 schematic Revised USB implementation Input protection diode + cap, added CW power supplies Removed interrupts from I2C devices to simplify routing Revisions to STM32 pins for bootloader and ESP8266 header

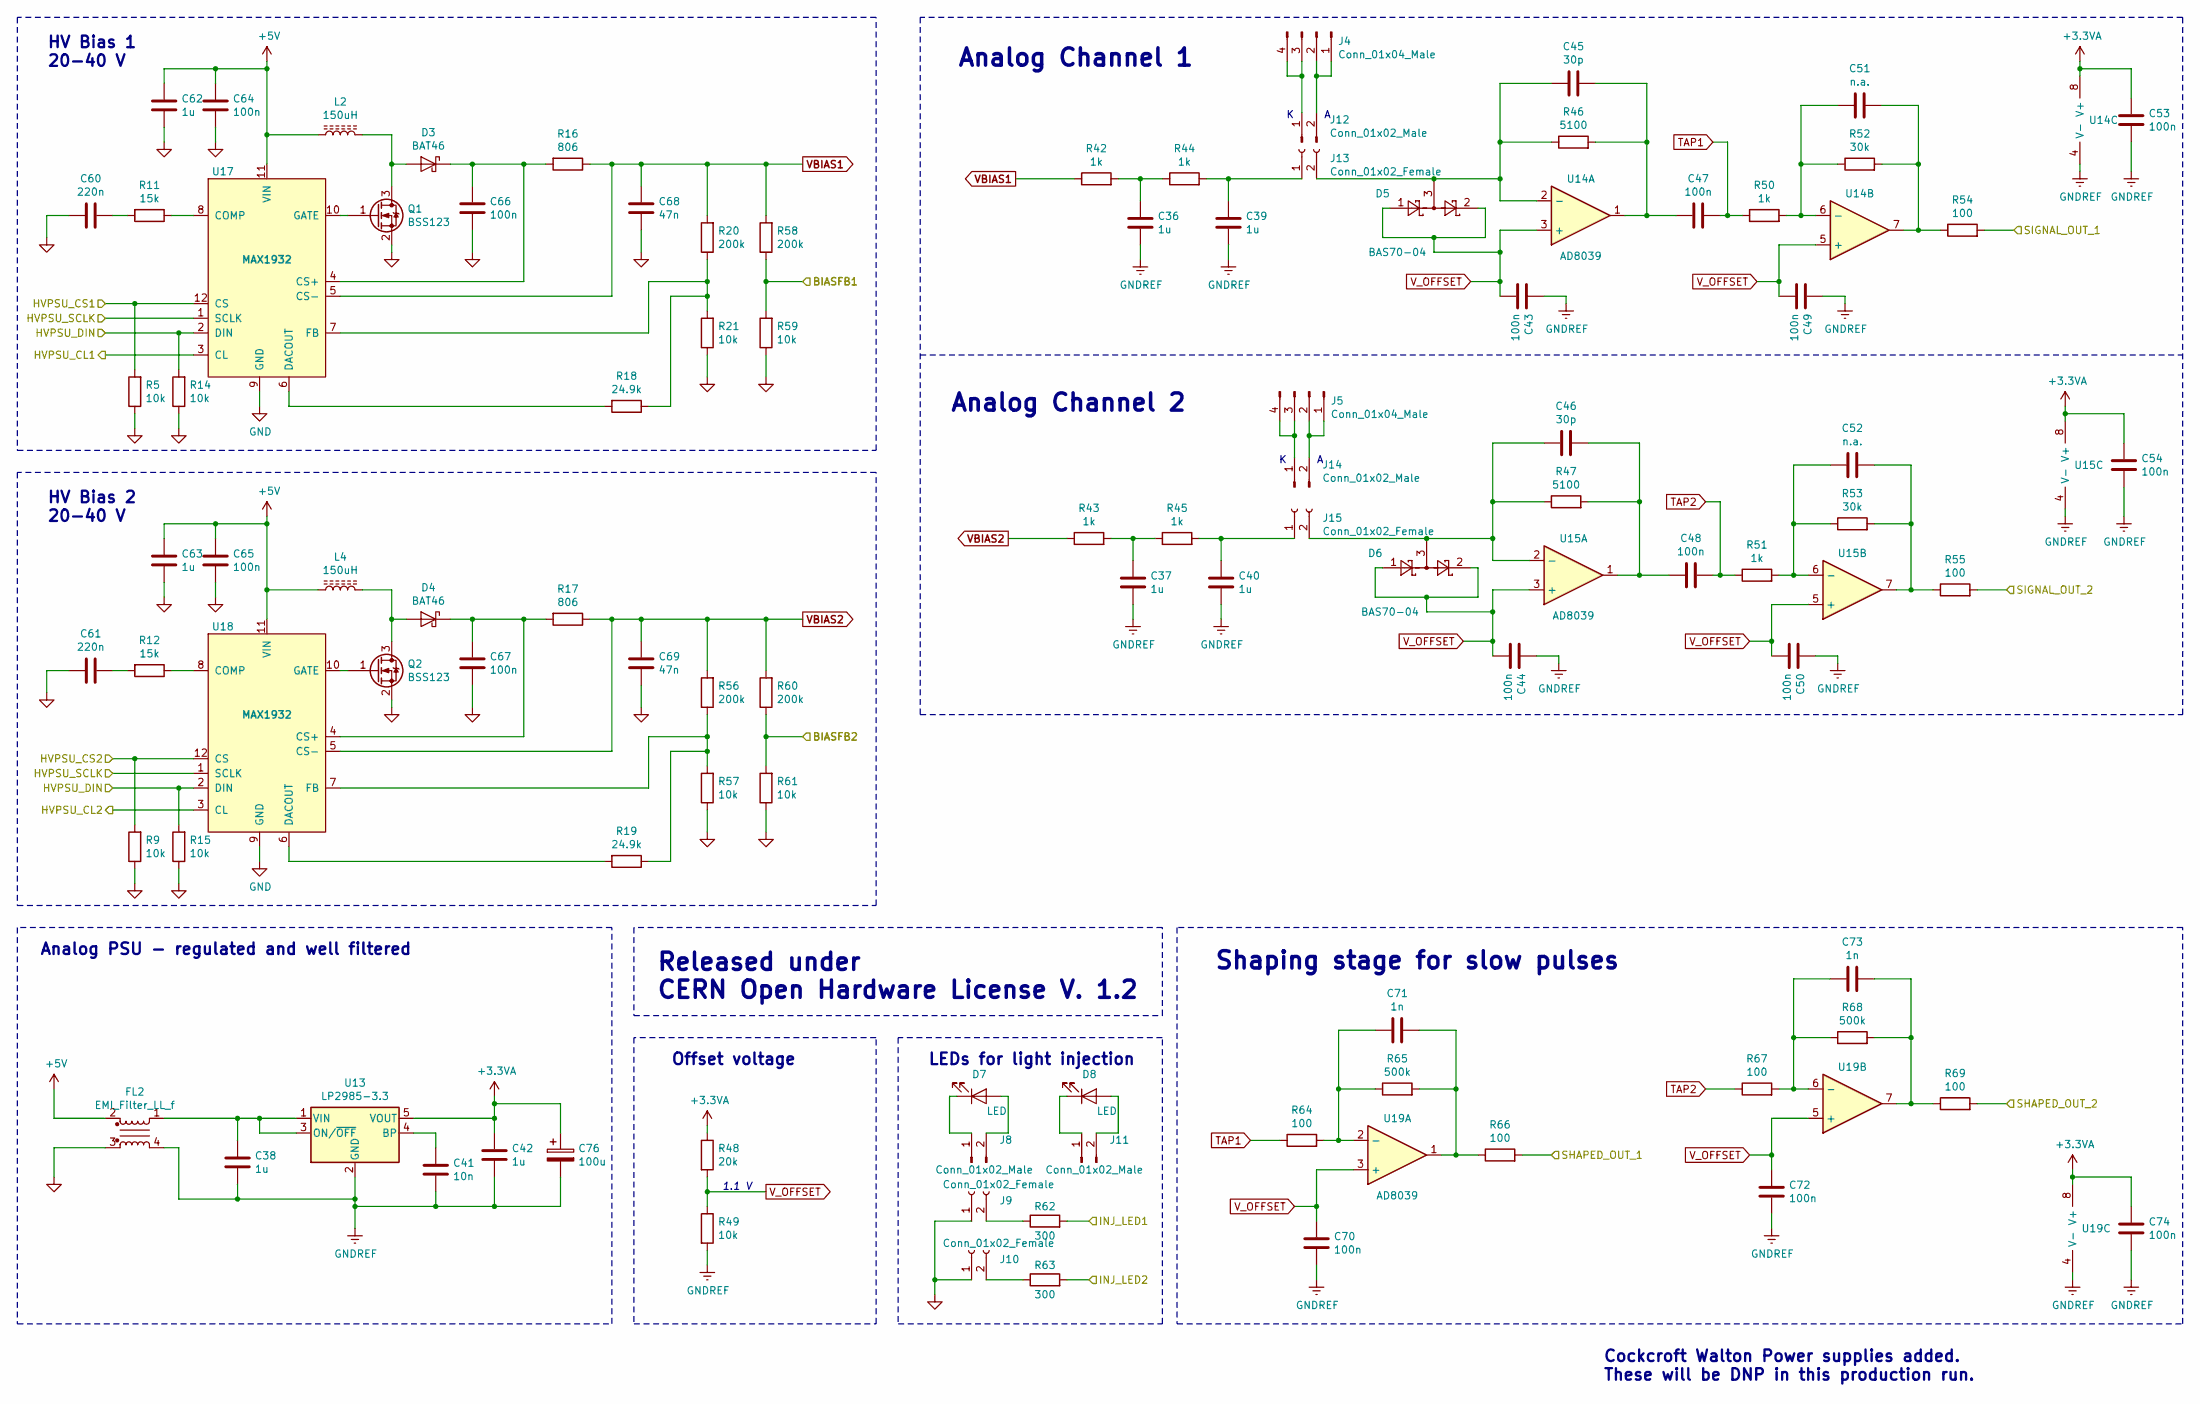
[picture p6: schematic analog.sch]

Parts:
C36, C37, C38, C39, C40, C42, C62, C63: 1u; C_1206_3216Metric
C41: 10n; C_0603_1608Metric
C43, C44, C49, C50, C53, C54, C64, C65, C66, C67, C70, C72, C74: 100n; C_0603_1608Metric
C45, C46: 30p; C_0603_1608Metric
C47, C48: 100n; C_0805_2012Metric
C51, C52: n.a.; C_1206_3216Metric
C60, C61: 220n; C_0603_1608Metric
C68, C69: 47n; C_0603_1608Metric
C71, C73: 1n; C_0603_1608Metric
C76: 100u; C_1206_3216Metric
D3, D4: BAT46; D_SOD-123F
D5, D6: BAS70-04; SOT-23
D7, D8: LED; LED_0603_1608Metric
FL2: EMI_Filter_LL_f; IND_744232090
J4, J5: Conn_01x04_Male; Ketek_PM3325-WB
J8, J11, J12, J14: Conn_01x02_Male; PinHeader_1x02_P2.54mm_Horizontal
J9, J10, J13, J15: Conn_01x02_Female; PinHeader_1x02_P2.54mm_Vertical
L2, L4: 150uH; L_1812_4532Metric
Q1, Q2: BSS123; SOT-23
R5, R9, R14, R15, R21, R49, R57, R59, R61: 10k; R_0603_1608Metric
R11, R12: 15k; R_0603_1608Metric
R16, R17: 806; R_0603_1608Metric
R18, R19: 24.9k; R_0603_1608Metric
R20, R56, R58, R60: 200k; R_0603_1608Metric
R42, R43, R44, R45, R50, R51: 1k; R_0603_1608Metric
R46, R47: 5100; R_0603_1608Metric
R48: 20k; R_0603_1608Metric
R52, R53: 30k; R_0603_1608Metric
R54, R55, R64, R66, R67, R69: 100; R_0603_1608Metric
R62, R63: 300; R_0603_1608Metric
R65, R68: 500k; R_0603_1608Metric
U13: LP2985-3.3; SOT-23-5
U14, U15, U19: AD8039; SOIC-8_3.9x4.9mm_P1.27mm
U17, U18: MAX1932; QFN-12-1EP_4x4mm_P0.8mm

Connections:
+3.3VA: C42.1, C53.1, C54.1, C74.1, C76.1, R48.1, U13.5 (VOUT), U14.8 (V+), U15.8 (V+), U19.8 (V+)
/analog/SIGNAL_OUT_1: R54.2; also elsewhere on the board
/analog/SIGNAL_OUT_2: R55.2; also elsewhere on the board
BIASFB1: R58.1, R59.2; also elsewhere on the board
BIASFB2: R60.1, R61.2; also elsewhere on the board
GND: C60.2, C61.2, C62.2, C63.2, C64.2, C65.2, C66.2, C67.2, C68.2, C69.2, FL2.3, J9.1, J10.1, Q1.2 (S), Q2.2 (S), R5.1, R9.1, R14.1, R15.1, R21.1, R57.1, R59.1, R61.1, U17.9 (GND), U18.9 (GND); also elsewhere on the board
GNDREF: C36.2, C37.2, C38.2, C39.2, C40.2, C41.2, C42.2, C43.1, C44.1, C49.1, C50.1, C53.2, C54.2, C70.2, C72.2, C74.2, C76.2, FL2.4, R49.2, U13.2 (GND), U14.4 (V-), U15.4 (V-), U19.4 (V-)
HVPSU_CL1: U17.3 (CL); also elsewhere on the board
HVPSU_CL2: U18.3 (CL); also elsewhere on the board
HVPSU_CS1: R5.2, U17.12 (CS); also elsewhere on the board
HVPSU_CS2: R9.2, U18.12 (CS); also elsewhere on the board
HVPSU_DIN: R14.2, R15.2, U17.2 (DIN), U18.2 (DIN); also elsewhere on the board
HVPSU_SCLK: U17.1 (SCLK), U18.1 (SCLK); also elsewhere on the board
INJ_LED1: R62.2, R63.2; also elsewhere on the board
unnamed: C36.1, R42.2, R44.1
unnamed: C37.1, R43.2, R45.1
unnamed: C38.1, FL2.1, U13.1 (VIN), U13.3 (ON/~OFF~)
unnamed: C39.1, J13.1, R44.2
unnamed: C40.1, J15.1, R45.2
unnamed: C41.1, U13.4 (BP)
unnamed: C45.1, C47.2, R46.2, U14.1
unnamed: C45.2, D5.3, J13.2, R46.1, U14.2 (-)
unnamed: C46.1, C48.2, R47.2, U15.1
unnamed: C46.2, D6.3, J15.2, R47.1, U15.2 (-)
unnamed: C51.1, R52.2, R54.1, U14.7
unnamed: C51.2, R50.2, R52.1, U14.6 (-)
unnamed: C52.1, R53.2, R55.1, U15.7
unnamed: C52.2, R51.2, R53.1, U15.6 (-)
unnamed: C60.1, R11.2
unnamed: C61.1, R12.2
unnamed: C66.1, D3.1 (K), R16.2, U17.4 (CS+)
unnamed: C67.1, D4.1 (K), R17.2, U18.4 (CS+)
unnamed: C71.1, R65.2, R66.1, U19.1
unnamed: C71.2, R64.2, R65.1, U19.2 (-)
unnamed: C73.1, R68.2, R69.1, U19.7
unnamed: C73.2, R67.2, R68.1, U19.6 (-)
unnamed: D3.2 (A), L2.2, Q1.3 (D)
unnamed: D4.2 (A), L4.2, Q2.3 (D)
unnamed: D7.1 (K), J8.1
unnamed: D7.2 (A), J8.2
unnamed: D8.1 (K), J11.1
unnamed: D8.2 (A), J11.2
unnamed: J9.2, R62.1
unnamed: J10.2, R63.1
unnamed: J4.3, J4.4, J12.1
unnamed: J4.1, J4.2, J12.2
unnamed: J5.3, J5.4, J14.1
unnamed: J5.1, J5.2, J14.2
unnamed: Q1.1 (G), U17.10 (GATE)
unnamed: Q2.1 (G), U18.10 (GATE)
unnamed: R11.1, U17.8 (COMP)
unnamed: R12.1, U18.8 (COMP)
unnamed: R18.1, R20.1, R21.2, U17.7 (FB)
unnamed: R18.2, U17.6 (DACOUT)
unnamed: R19.1, R56.1, R57.2, U18.7 (FB)
unnamed: R19.2, U18.6 (DACOUT)
SHAPED_OUT_1: R66.2; also elsewhere on the board
SHAPED_OUT_2: R69.2; also elsewhere on the board
TAP1: C47.1, R50.1, R64.1
TAP2: C48.1, R51.1, R67.1
VBIAS1: C68.1, R16.1, R20.2, R42.1, R58.2, U17.5 (CS-)
VBIAS2: C69.1, R17.1, R43.1, R56.2, R60.2, U18.5 (CS-)
V_OFFSET: C43.2, C44.2, C49.2, C50.2, C70.1, C72.1, D5.1, D5.2, D6.1, D6.2, R48.2, R49.1, U14.3 (+), U14.5 (+), U15.3 (+), U15.5 (+), U19.3 (+), U19.5 (+)

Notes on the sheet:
Analog Channel 1
Analog Channel 2
Analog PSU - regulated and well filtered
Offset voltage
1.1 V
HV Bias 1 20-40 V
HV Bias 2 20-40 V
Released under CERN Open Hardware License V. 1.2
Shaping stage for slow pulses
LEDs for light injection
Cockcroft Walton Power supplies added. These will be DNP in this production run.

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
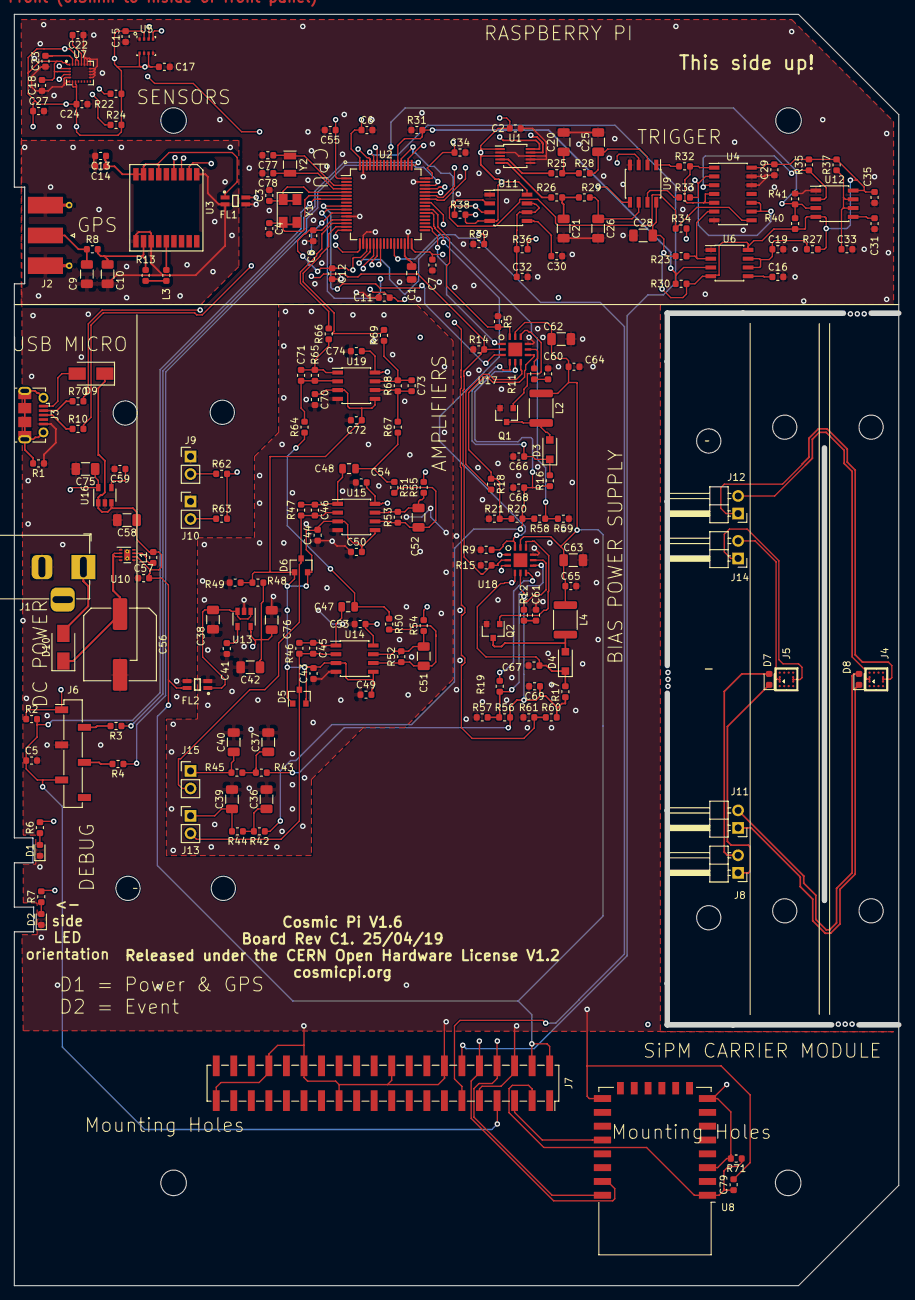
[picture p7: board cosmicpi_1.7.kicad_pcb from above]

Board: 4 copper layers, 128.0 x 184.0 mm, 208 parts (0 on the bottom side), 130 nets.

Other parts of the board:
H1, H2, H3, H3#2: MountingHole_3.7mm

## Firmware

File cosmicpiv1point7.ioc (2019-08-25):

#MicroXplorer Configuration settings - do not modify
ADC1.Channel-0\#ChannelRegularConversion=ADC_CHANNEL_0
ADC1.IPParameters=Rank-0\#ChannelRegularConversion,master,Channel-0\#ChannelRegularConversion,SamplingTime-0\#ChannelRegularConversion,NbrOfConversionFlag
ADC1.NbrOfConversionFlag=1
ADC1.Rank-0\#ChannelRegularConversion=1
ADC1.SamplingTime-0\#ChannelRegularConversion=ADC_SAMPLETIME_3CYCLES
ADC1.master=1
File.Version=6
KeepUserPlacement=false
Mcu.Family=STM32F4
Mcu.IP0=ADC1
Mcu.IP1=I2C1
Mcu.IP2=NVIC
Mcu.IP3=RCC
Mcu.IP4=SYS
Mcu.IP5=TIM2
Mcu.IP6=TIM3
Mcu.IP7=USART1
Mcu.IP8=USART2
Mcu.IP9=USB_OTG_FS
Mcu.IPNb=10
Mcu.Name=STM32F401R(D-E)Tx
Mcu.Package=LQFP64
Mcu.Pin0=PC14-OSC32_IN
Mcu.Pin1=PC15-OSC32_OUT
Mcu.Pin10=PA3
Mcu.Pin11=PA4
Mcu.Pin12=PA5
Mcu.Pin13=PA6
Mcu.Pin14=PA7
Mcu.Pin15=PB1
Mcu.Pin16=PB13
Mcu.Pin17=PC7
Mcu.Pin18=PC8
Mcu.Pin19=PA8
Mcu.Pin2=PH0 - OSC_IN
Mcu.Pin20=PA9
Mcu.Pin21=PA10
Mcu.Pin22=PA11
Mcu.Pin23=PA12
Mcu.Pin24=PA13
Mcu.Pin25=PA14
Mcu.Pin26=PA15
Mcu.Pin27=PC11
Mcu.Pin28=PC12
Mcu.Pin29=PB3
Mcu.Pin3=PH1 - OSC_OUT
Mcu.Pin30=PB7
Mcu.Pin31=PB8
Mcu.Pin32=VP_ADC1_TempSens_Input
Mcu.Pin33=VP_SYS_VS_Systick
Mcu.Pin34=VP_TIM2_VS_ClockSourceINT
Mcu.Pin35=VP_TIM3_VS_ClockSourceINT
Mcu.Pin4=PC1
Mcu.Pin5=PC2
Mcu.Pin6=PC3
Mcu.Pin7=PA0-WKUP
Mcu.Pin8=PA1
Mcu.Pin9=PA2
Mcu.PinsNb=36
Mcu.ThirdPartyNb=0
Mcu.UserConstants=
Mcu.UserName=STM32F401RETx
MxCube.Version=5.2.1
MxDb.Version=DB.5.0.21
NVIC.BusFault_IRQn=true\:0\:0\:false\:false\:true\:false\:false
NVIC.DebugMonitor_IRQn=true\:0\:0\:false\:false\:true\:false\:false
NVIC.HardFault_IRQn=true\:0\:0\:false\:false\:true\:false\:false
NVIC.MemoryManagement_IRQn=true\:0\:0\:false\:false\:true\:false\:false
NVIC.NonMaskableInt_IRQn=true\:0\:0\:false\:false\:true\:false\:false
NVIC.PendSV_IRQn=true\:0\:0\:false\:false\:true\:false\:false
NVIC.PriorityGroup=NVIC_PRIORITYGROUP_4
NVIC.SVCall_IRQn=true\:0\:0\:false\:false\:true\:false\:false
NVIC.SysTick_IRQn=true\:0\:0\:false\:false\:true\:false\:true
NVIC.UsageFault_IRQn=true\:0\:0\:false\:false\:true\:false\:false
PA0-WKUP.GPIOParameters=GPIO_Label
PA0-WKUP.GPIO_Label=shaped_out_1
PA0-WKUP.Locked=true
PA0-WKUP.Signal=ADCx_IN0
PA1.GPIOParameters=GPIO_Label
PA1.GPIO_Label=shaped_out_2
PA1.Locked=true
PA1.Signal=ADCx_IN1
PA10.Locked=true
PA10.Mode=Asynchronous
PA10.Signal=USART1_RX
PA11.Locked=true
PA11.Mode=Device_Only
PA11.Signal=USB_OTG_FS_DM
PA12.Locked=true
PA12.Mode=Device_Only
PA12.Signal=USB_OTG_FS_DP
PA13.Locked=true
PA13.Mode=Serial_Wire
PA13.Signal=SYS_JTMS-SWDIO
PA14.Locked=true
PA14.Mode=Serial_Wire
PA14.Signal=SYS_JTCK-SWCLK
PA15.GPIOParameters=GPIO_Label
PA15.GPIO_Label=GPSPPS
PA15.Locked=true
PA15.Signal=S_TIM2_CH1_ETR
PA2.GPIOParameters=GPIO_Label
PA2.GPIO_Label=gpsrx
PA2.Locked=true
PA2.Mode=Asynchronous
PA2.Signal=USART2_TX
PA3.GPIOParameters=GPIO_Label
PA3.GPIO_Label=gpstx
PA3.Locked=true
PA3.Mode=Asynchronous
PA3.Signal=USART2_RX
PA4.GPIOParameters=GPIO_Label
PA4.GPIO_Label=biasfb1
PA4.Locked=true
PA4.Signal=ADCx_IN4
PA5.GPIOParameters=GPIO_Label
PA5.GPIO_Label=biasfb2
PA5.Locked=true
PA5.Signal=ADCx_IN5
PA6.GPIOParameters=GPIO_Label
PA6.GPIO_Label=inj_led
PA6.Locked=true
PA6.Signal=S_TIM3_CH1
PA7.GPIOParameters=GPIO_Label
PA7.GPIO_Label=pwr_led
PA7.Locked=true
PA7.Signal=GPIO_Output
PA8.GPIOParameters=GPIO_Label
PA8.GPIO_Label=evt_led
PA8.Locked=true
PA8.Signal=GPIO_Output
PA9.Locked=true
PA9.Mode=Asynchronous
PA9.Signal=USART1_TX
PB1.GPIOParameters=GPIO_Label
PB1.GPIO_Label=flag
PB1.Locked=true
PB1.Signal=GPIO_Output
PB13.GPIOParameters=GPIO_Label
PB13.GPIO_Label=hvpsu_sclk
PB13.Locked=true
PB13.Signal=GPIO_Output
PB3.GPIOParameters=GPIO_Label
PB3.GPIO_Label=trig_out
PB3.Locked=true
PB3.Signal=S_TIM2_CH2
PB7.Locked=true
PB7.Mode=I2C
PB7.Signal=I2C1_SDA
PB8.Locked=true
PB8.Mode=I2C
PB8.Signal=I2C1_SCL
PC1.GPIOParameters=GPIO_Label
PC1.GPIO_Label=hvpsu_cl1
PC1.Locked=true
PC1.Signal=GPIO_Input
PC11.GPIOParameters=GPIO_Label
PC11.GPIO_Label=strigout_b
PC11.Locked=true
PC11.Signal=GPIO_Input
PC12.GPIOParameters=GPIO_Label
PC12.GPIO_Label=strigout_a
PC12.Locked=true
PC12.Signal=GPIO_Input
PC14-OSC32_IN.Locked=true
PC14-OSC32_IN.Mode=LSE-External-Oscillator
PC14-OSC32_IN.Signal=RCC_OSC32_IN
PC15-OSC32_OUT.Locked=true
PC15-OSC32_OUT.Mode=LSE-External-Oscillator
PC15-OSC32_OUT.Signal=RCC_OSC32_OUT
PC2.GPIOParameters=GPIO_Label
PC2.GPIO_Label=hvpsu_cl2
PC2.Locked=true
PC2.Signal=GPIO_Input
PC3.GPIOParameters=GPIO_Label
PC3.GPIO_Label=hvpsu_din
PC3.Locked=true
PC3.Signal=GPIO_Output
PC7.GPIOParameters=GPIO_Label
PC7.GPIO_Label=hvpsu_cs2
PC7.Locked=true
PC7.Signal=GPIO_Output
PC8.GPIOParameters=GPIO_Label
PC8.GPIO_Label=hvpsu_cs1
PC8.Locked=true
PC8.Signal=GPIO_Output
PCC.Checker=false
PCC.Line=STM32F401
PCC.MCU=STM32F401R(D-E)Tx
PCC.PartNumber=STM32F401RETx
PCC.Seq0=0
PCC.Series=STM32F4
PCC.Temperature=25
PCC.Vdd=3.3
PH0\ -\ OSC_IN.Locked=true
PH0\ -\ OSC_IN.Mode=HSE-External-Oscillator
PH0\ -\ OSC_IN.Signal=RCC_OSC_IN
PH1\ -\ OSC_OUT.Locked=true
PH1\ -\ OSC_OUT.Mode=HSE-External-Oscillator
PH1\ -\ OSC_OUT.Signal=RCC_OSC_OUT
PinOutPanel.RotationAngle=0
ProjectManager.AskForMigrate=true
ProjectManager.BackupPrevious=false
ProjectManager.CompilerOptimize=6
ProjectManager.ComputerToolchain=false
ProjectManager.CoupleFile=false
ProjectManager.CustomerFirmwarePackage=
ProjectManager.DefaultFWLocation=true
ProjectManager.DeletePrevious=true
ProjectManager.DeviceId=STM32F401RETx
ProjectManager.FirmwarePackage=STM32Cube FW_F4 V1.24.1
ProjectManager.FreePins=false
ProjectManager.HalAssertFull=false
ProjectManager.HeapSize=0x200
ProjectManager.KeepUserCode=true
ProjectManager.LastFirmware=true
ProjectManager.LibraryCopy=0
ProjectManager.MainLocation=Src
ProjectManager.NoMain=false
ProjectManager.PreviousToolchain=
ProjectManager.ProjectBuild=false
ProjectManager.ProjectFileName=cosmicpiv1point7.ioc
ProjectManager.ProjectName=cosmicpiv1point7
ProjectManager.StackSize=0x400
ProjectManager.TargetToolchain=EWARM V8
ProjectManager.ToolChainLocation=
ProjectManager.UnderRoot=false
ProjectManager.functionlistsort=1-SystemClock_Config-RCC-false-HAL-false
RCC.48MHZClocksFreq_Value=48000000
RCC.AHBFreq_Value=84000000
RCC.APB1CLKDivider=RCC_HCLK_DIV2
RCC.APB1Freq_Value=42000000
RCC.APB1TimFreq_Value=84000000
RCC.APB2Freq_Value=84000000
RCC.APB2TimFreq_Value=84000000
RCC.CortexFreq_Value=84000000
RCC.FCLKCortexFreq_Value=84000000
RCC.HCLKFreq_Value=84000000
RCC.HSE_VALUE=20000000
RCC.HSI_VALUE=16000000
RCC.I2SClocksFreq_Value=192000000
RCC.IPParameters=48MHZClocksFreq_Value,AHBFreq_Value,APB1CLKDivider,APB1Freq_Value,APB1TimFreq_Value,APB2Freq_Value,APB2TimFreq_Value,CortexFreq_Value,FCLKCortexFreq_Value,HCLKFreq_Value,HSE_VALUE,HSI_VALUE,I2SClocksFreq_Value,LSI_VALUE,MCO2PinFreq_Value,PLLCLKFreq_Value,PLLM,PLLN,PLLP,PLLQ,PLLQCLKFreq_Value,RTCFreq_Value,RTCHSEDivFreq_Value,SYSCLKFreq_VALUE,SYSCLKSource,VCOI2SOutputFreq_Value,VCOInputFreq_Value,VCOOutputFreq_Value,VcooutputI2S
RCC.LSI_VALUE=32000
RCC.MCO2PinFreq_Value=84000000
RCC.PLLCLKFreq_Value=84000000
RCC.PLLM=10
RCC.PLLN=168
RCC.PLLP=RCC_PLLP_DIV4
RCC.PLLQ=7
RCC.PLLQCLKFreq_Value=48000000
RCC.RTCFreq_Value=32000
RCC.RTCHSEDivFreq_Value=10000000
RCC.SYSCLKFreq_VALUE=84000000
RCC.SYSCLKSource=RCC_SYSCLKSOURCE_PLLCLK
RCC.VCOI2SOutputFreq_Value=384000000
RCC.VCOInputFreq_Value=2000000
RCC.VCOOutputFreq_Value=336000000
RCC.VcooutputI2S=192000000
SH.ADCx_IN0.0=ADC1_IN0,IN0
SH.ADCx_IN0.ConfNb=1
SH.ADCx_IN1.0=ADC1_IN1,IN1
SH.ADCx_IN1.ConfNb=1
SH.ADCx_IN4.0=ADC1_IN4,IN4
SH.ADCx_IN4.ConfNb=1
SH.ADCx_IN5.0=ADC1_IN5,IN5
SH.ADCx_IN5.ConfNb=1
SH.S_TIM2_CH1_ETR.0=TIM2_CH1,Input_Capture1_from_TI1
SH.S_TIM2_CH1_ETR.ConfNb=1
SH.S_TIM2_CH2.0=TIM2_CH2,Input_Capture2_from_TI2
SH.S_TIM2_CH2.ConfNb=1
SH.S_TIM3_CH1.0=TIM3_CH1,PWM Generation1 CH1
SH.S_TIM3_CH1.ConfNb=1
TIM2.Channel-Input_Capture1_from_TI1=TIM_CHANNEL_1
TIM2.Channel-Input_Capture2_from_TI2=TIM_CHANNEL_2
TIM2.IPParameters=Channel-Input_Capture1_from_TI1,Channel-Input_Capture2_from_TI2
TIM3.Channel-PWM\ Generation1\ CH1=TIM_CHANNEL_1
TIM3.IPParameters=Channel-PWM Generation1 CH1
USART1.IPParameters=VirtualMode
USART1.VirtualMode=VM_ASYNC
USART2.IPParameters=VirtualMode
USART2.VirtualMode=VM_ASYNC
USB_OTG_FS.IPParameters=VirtualMode
USB_OTG_FS.VirtualMode=Device_Only
VP_ADC1_TempSens_Input.Mode=IN-TempSens
VP_ADC1_TempSens_Input.Signal=ADC1_TempSens_Input
VP_SYS_VS_Systick.Mode=SysTick
VP_SYS_VS_Systick.Signal=SYS_VS_Systick
VP_TIM2_VS_ClockSourceINT.Mode=Internal
VP_TIM2_VS_ClockSourceINT.Signal=TIM2_VS_ClockSourceINT
VP_TIM3_VS_ClockSourceINT.Mode=Internal
VP_TIM3_VS_ClockSourceINT.Signal=TIM3_VS_ClockSourceINT
board=custom

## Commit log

2019-08-25 First upload - schematic only
    Schematic updates for the V1.7 production run.
    Changes to:
    USB connection (dropped OTG, slave device only, 5V power now connected)
    Dropped interrupts from I2C devices to facilitate routing
    Swapped to BME280 temperature, pressure and humidity sensor
    Added input protection diode and increased capacitor on DC input to allow use of AC supplies
    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
    [analog.sch, cosmicpi_1.7.kicad_pcb, cosmicpi_1.7.sch]
2019-08-26 added esp header and cw psu
    footpints and board layouts to do
    [analog.sch]
2019-09-03 updated a little
    [cosmicpi_1.7.kicad_pcb, cosmicpi_1.7.sch]
2019-09-15 footprints corrected, routing in progress
    [analog.sch, cosmicpi_1.7.kicad_pcb]
2019-09-29 finished place and route
    BOM still needs updating!
    [cosmicpi_1.7.kicad_pcb]
2019-11-01 added BOM for 1.7
    [CosmicPiBom1point7extended.xlsx, cosmicpi_1.6_enhanced.xlsx, cosmicpi_1.7-B_Cu.gbr, cosmicpi_1.7-B_Mask.gbr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]

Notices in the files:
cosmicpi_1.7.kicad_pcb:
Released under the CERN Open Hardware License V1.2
